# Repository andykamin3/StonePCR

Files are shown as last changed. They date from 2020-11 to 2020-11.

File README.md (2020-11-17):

# StonePCR
*Por Joaquín Alonso, Manuel Agustín Gonzalez y Andrés Kaminker*

## Introducción

### ¿Qué es una máquina de PCR?
También conocido como termociclador es un elemento esencial en laboratorios de biología molecular dado que permite realizar, los ciclos térmicos esenciales en la reacción en cadena de la polimerasa. Es por esto que son utilizados en múltiples procesos, uno de ellos es el test de COVID-19. 
Estos equipos pueden llegar a costar entre 2 y 50 mil dólares en nuestro [país](https://www.onelab.com.ar/pcr). Pese a eso existen alternativas libres como [OpenPCR](https://openpcr.org/) que resultan mucho más baratas. Este es un trabajo que busca ofrecer una alternativa similar a OpenPCR pero con mejores prestaciones a nivel técnico. 

## Selección de Componentes

### ARM Cortex M3

Este microcontrolador fue elegido dado que representaba un improvement por sobre el Atmega328 del OpenPCR. A su vez contaba con pines que soportaban los protocolos necesarios tal como I2C y SPI. Por último contaba con pines que soportaban la interfaz casi directa con un puerto USB, elemento altamente deseable para evitar complicaciones en el desarrollo de la interfaz. Por último, el ADC integrado era suficiente para la lectura de los sensores, proporcionando la precisión suficiente. 
- [Datasheet](https://www.st.com/resource/en/datasheet/stm32f102c8.pdf)
- [Guía de Comienzo Rápido](https://www.st.com/resource/en/application_note/cd00164185-getting-started-with-stm32f10xxx-hardware-development-stmicroelectronics.pdf)

### Comunicación con dispositivos externos

#### USB

En primer lugar dispusimos ofrecer comunicación con una computadora mediante USB-B Micro. De esta manera permitíamos el uso del mismo con un conector fácilmente disponible pero que no agregaba las consideraciones de diseño necesarias del estándar USB-C dado que las prestaciones ofrecidas por este(mayor velocidad y _power delivery_ no fueron consideradas necesarias). Esta interfaz tiene como objetivo ofrecer una configuración rápida y fácil desde la aplicación complementaria en el ordenador. 

#### Bluetooth

Aunque la conexión USB era suficiente, decidimos agregar un módulo Bluetooth (HC-05) que permita la conexión inalámbrica a una app _companion_ en un teléfono celular que facilite el trabajo del usuario y le ofrezca recordatorios y alarmas sin tener que estar permanentemente alerta. 

### Sensado de Temperatura

Para el sensado de temperatura decidimos utilizar termistores NTC ofrecidos por Vishay(Modelo: (NTCLE317E4103SBA [https://www.vishay.com/docs/29216/ntcle317e4103sba.pdf]) que tenían las características técnicas necesarias, especialmente la precisión. A través de un divisor resistivo y el ADC del ARM Cortex M3 obtenemos el valor de temperatura, necesario para realizar correctamente los ciclos térmicos. 

### Placas de Peltier y Drivers

Las placas de Peltier seleccionadas, componente esencial del sistema, fueron un componente complejo de seleccionar pero finalmente nos decantamos por [VT-127-1.0-1.3-71](https://tetech.com/wp-content/uploads/2019/03/VT-127-1.0-1.3-71.pdf) de Tetech. La temperatura soportada y la alta potencia que manejan las convirtieron en una opción idónea para el proceso seleccionado. Los drivers fueron seleccionados en función a las placas de Peltier y sus altos requerimientos eléctricos. Es por eso que el driver [VNH5019A](https://www.pololu.com/product/1449) de Pololu fue seleccionadop porque podía entregar la potencia necesaria y era relativamente asequible. 

### Módulo de Pantalla

Para simplificar el desarrollo de la interfaz de usuario y prescindir de una miríada de botones y perillas decidimos usar una pantalla táctil. Para ello fue seleccionado el módulo de Adafruit [ILI9341](https://www.adafruit.com/product/2478). De esta manera disponemos de una pantalla sin incurrir en complejidades extras.

### Alimentación

Debido a la complejidad que presenta la placa y siguiendo los pasos de OpenPCR nos decantamos por el uso de un conector ATX-24 y una fuente externa lo que facilita el routeo y nos provee de líneas de alimentación con poco ruido en 3.3V y 12V.

## Tareas Pendientes 

- [x] Esquemático
- [x] Placement
- Routeo

## Imágenes

Render 3D del PCB
- Render del PCB en 3D

## Instrucciones de Uso del Proyecto
- Realizar una descarga o clonar el repositorio de forma local
- Abrir usando KiCad 5.1.6

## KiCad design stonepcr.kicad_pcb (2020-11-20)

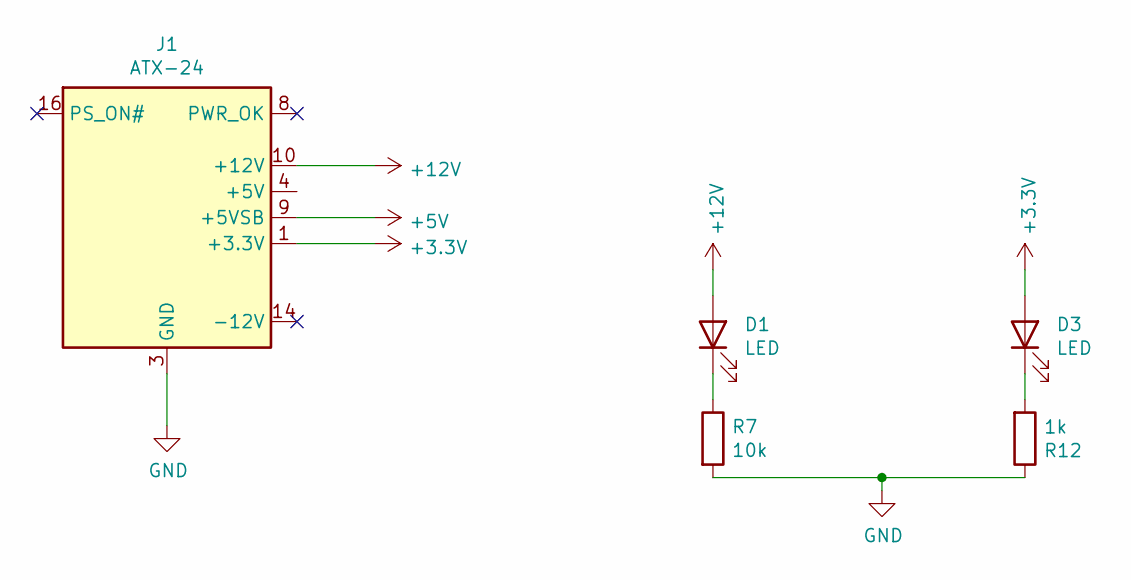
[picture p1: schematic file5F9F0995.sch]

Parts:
D1, D3: LED; LED_0805_2012Metric
J1: ATX-24; Molex_Mini-Fit_Jr_5566-24A_2x12_P4.20mm_Vertical
R7: 10k; R_0805_2012Metric
R12: 1k; R_0805_2012Metric

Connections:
+3V3: D3.2 (A), J1.1 (+3.3V), J1.2 (+3.3V), J1.12 (+3.3V), J1.13 (+3.3V); also elsewhere on the board
+5V: J1.9 (+5VSB)
+12V: D1.2 (A), J1.10 (+12V), J1.11 (+12V); also elsewhere on the board
GND: J1.3 (GND), J1.5 (GND), J1.7 (GND), J1.15 (GND), J1.17 (GND), J1.18 (GND), J1.19 (GND), J1.24 (GND), R7.2, R12.1; also elsewhere on the board
unnamed: D1.1 (K), R7.1
unnamed: D3.1 (K), R12.2
unnamed: J1.4 (+5V), J1.6 (+5V), J1.21 (+5V), J1.22 (+5V), J1.23 (+5V)

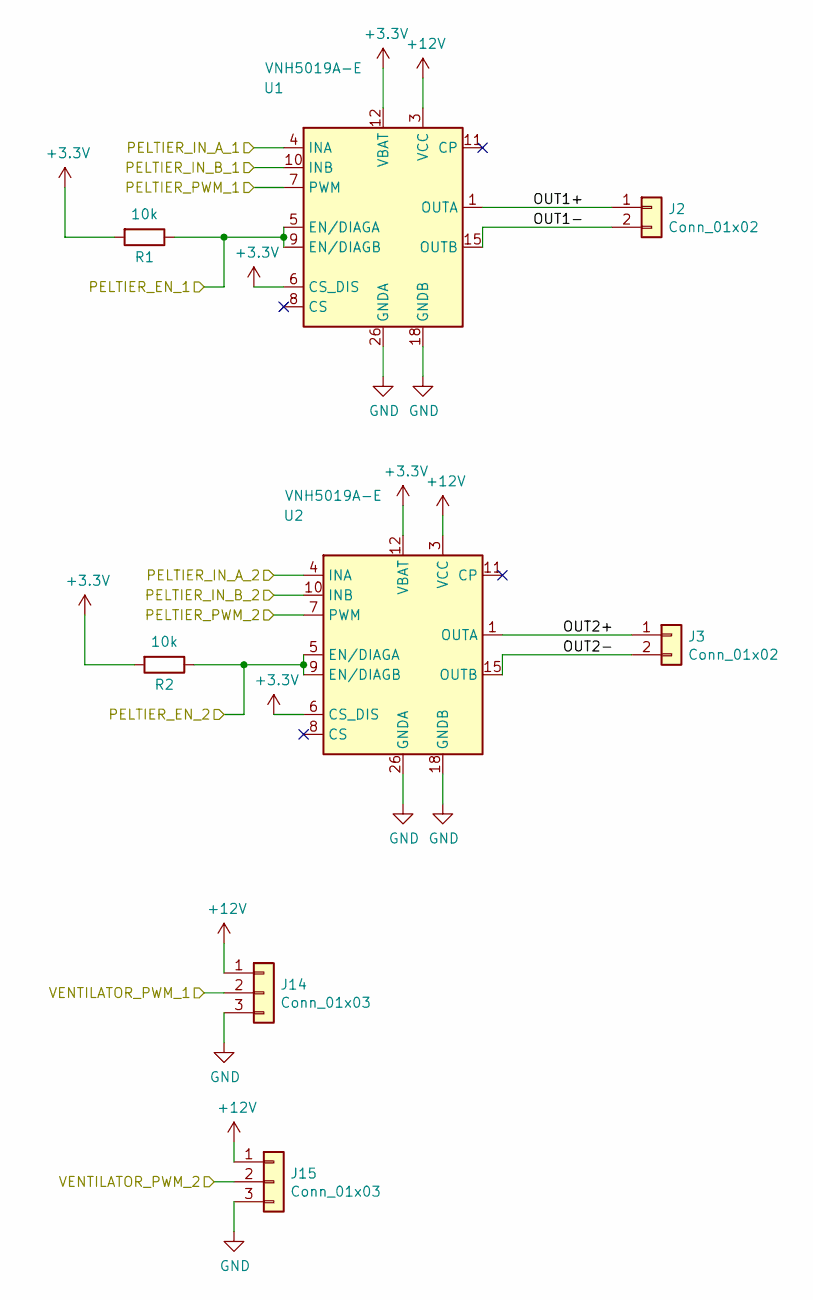
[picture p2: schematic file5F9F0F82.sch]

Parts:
J2, J3: Conn_01x02; Molex_Sabre_43160-0102_1x02_P7.49mm_Vertical_ThermalVias
J14, J15: Conn_01x03; PinSocket_1x03_P2.54mm_Vertical
R1, R2: 10k; R_0805_2012Metric
U1, U2: VNH5019A-E; ST_MultiPowerSO-30

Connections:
+3V3: R1.2, R2.2, U1.6 (CS_DIS), U1.12 (VBAT), U2.6 (CS_DIS), U2.12 (VBAT); also elsewhere on the board
+12V: J14.1, J15.1, U1.3 (VCC), U1.13 (VCC), U1.23 (VCC), U1.31 (VCC), U2.3 (VCC), U2.13 (VCC), U2.23 (VCC), U2.31 (VCC); also elsewhere on the board
/ControllerSchematic/PELTIER_EN_1: R1.1, U1.5 (EN/DIAGA), U1.9 (EN/DIAGB); also elsewhere on the board
/ControllerSchematic/PELTIER_EN_2: R2.1, U2.5 (EN/DIAGA), U2.9 (EN/DIAGB); also elsewhere on the board
/ControllerSchematic/PELTIER_IN_A_1: U1.4 (INA); also elsewhere on the board
/ControllerSchematic/PELTIER_IN_A_2: U2.4 (INA); also elsewhere on the board
/ControllerSchematic/PELTIER_IN_B_1: U1.10 (INB); also elsewhere on the board
/ControllerSchematic/PELTIER_IN_B_2: U2.10 (INB); also elsewhere on the board
/ControllerSchematic/PELTIER_PWM_1: U1.7 (PWM); also elsewhere on the board
/ControllerSchematic/PELTIER_PWM_2: U2.7 (PWM); also elsewhere on the board
/ControllerSchematic/VENTILADOR_PWM_1: J15.2; also elsewhere on the board
/ControllerSchematic/VENTILADOR_PWM_2: J14.2; also elsewhere on the board
/PeltierSchematic/OUT1+: J2.1, U1.1 (OUTA), U1.25 (OUTA), U1.30 (OUTA), U1.33 (OUTA)
/PeltierSchematic/OUT1-: J2.2, U1.15 (OUTB), U1.16 (OUTB), U1.21 (OUTB), U1.32 (OUTB)
/PeltierSchematic/OUT2+: J3.1, U2.1 (OUTA), U2.25 (OUTA), U2.30 (OUTA), U2.33 (OUTA)
/PeltierSchematic/OUT2-: J3.2, U2.15 (OUTB), U2.16 (OUTB), U2.21 (OUTB), U2.32 (OUTB)
GND: J14.3, J15.3, U1.18 (GNDB), U1.19 (GNDB), U1.20 (GNDB), U1.26 (GNDA), U1.27 (GNDA), U1.28 (GNDA), U2.18 (GNDB), U2.19 (GNDB), U2.20 (GNDB), U2.26 (GNDA), U2.27 (GNDA), U2.28 (GNDA); also elsewhere on the board

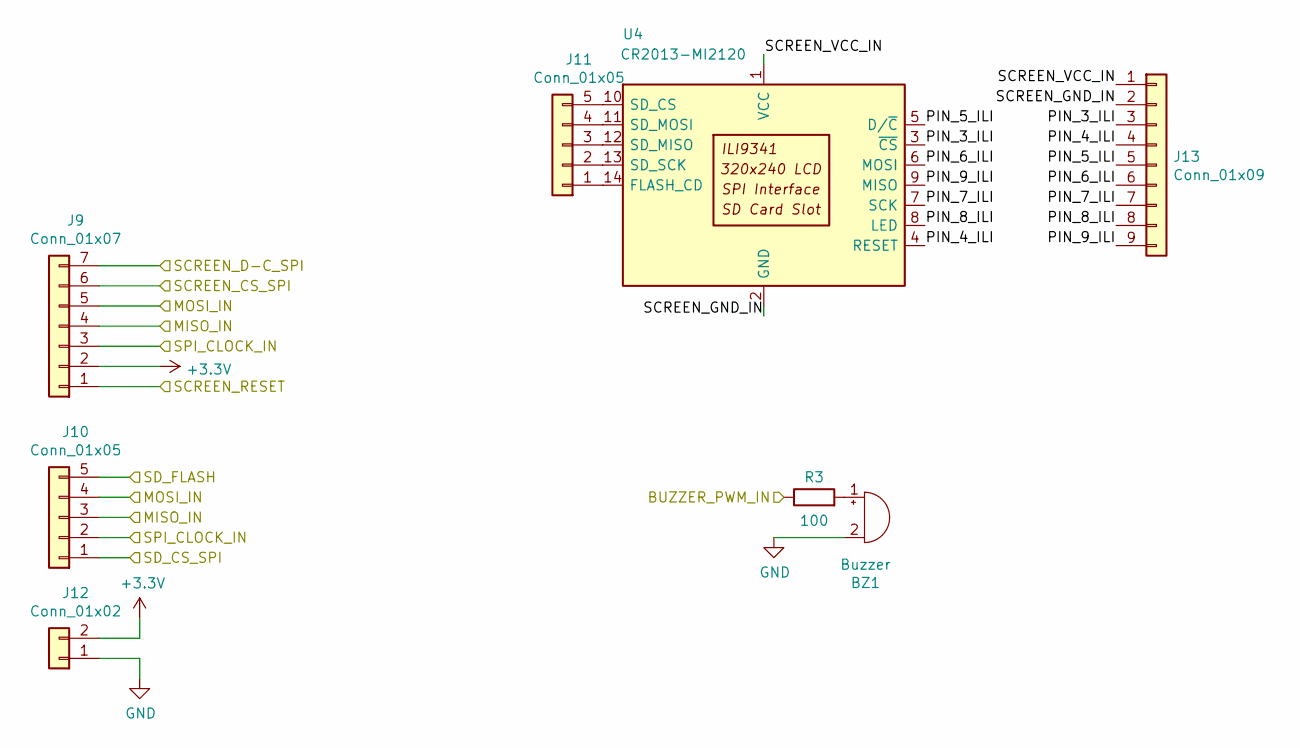
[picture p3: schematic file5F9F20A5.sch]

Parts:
BZ1: Buzzer; Buzzer_Mallory_AST1109MLTRQ
J9: Conn_01x07; PinSocket_1x07_P2.54mm_Vertical
J10, J11: Conn_01x05; PinSocket_1x05_P2.54mm_Vertical
J12: Conn_01x02; PinSocket_1x02_P2.54mm_Vertical
J13: Conn_01x09; PinSocket_1x09_P2.54mm_Vertical
R3: 100; R_0805_2012Metric
U4: CR2013-MI2120

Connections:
+3V3: J9.2, J12.2; also elsewhere on the board
/ControllerSchematic/BUZZER_PWM_IN: R3.1; also elsewhere on the board
/ControllerSchematic/SCREEN_CS_SPI: J9.6; also elsewhere on the board
/ControllerSchematic/SCREEN_D-C_SPI: J9.7; also elsewhere on the board
/ControllerSchematic/SCREEN_RESET: J9.1; also elsewhere on the board
/ControllerSchematic/SD_CS_SPI: J10.1; also elsewhere on the board
/ControllerSchematic/SD_FLASH: J10.5; also elsewhere on the board
/ControllerSchematic/SPI_CLOCK_IN: J9.3, J10.2; also elsewhere on the board
/DisplaySchematic/MISO_IN: J9.4, J10.3; also elsewhere on the board
/DisplaySchematic/MOSI_IN: J9.5, J10.4; also elsewhere on the board
/DisplaySchematic/PIN_3_ILI: J13.3, U4.3 (~CS)
/DisplaySchematic/PIN_4_ILI: J13.4, U4.4 (RESET)
/DisplaySchematic/PIN_5_ILI: J13.5, U4.5 (D/~C)
/DisplaySchematic/PIN_6_ILI: J13.6, U4.6 (MOSI)
/DisplaySchematic/PIN_7_ILI: J13.7, U4.7 (SCK)
/DisplaySchematic/PIN_8_ILI: J13.8, U4.8 (LED)
/DisplaySchematic/PIN_9_ILI: J13.9, U4.9 (MISO)
/DisplaySchematic/SCREEN_GND_IN: J13.2, U4.2 (GND)
/DisplaySchematic/SCREEN_VCC_IN: J13.1, U4.1 (VCC)
GND: BZ1.2 (+), J12.1; also elsewhere on the board
unnamed: BZ1.1 (-), R3.2
unnamed: J11.1, U4.14 (FLASH_CD)
unnamed: J11.2, U4.13 (SD_SCK)
unnamed: J11.3, U4.12 (SD_MISO)
unnamed: J11.4, U4.11 (SD_MOSI)
unnamed: J11.5, U4.10 (SD_CS)

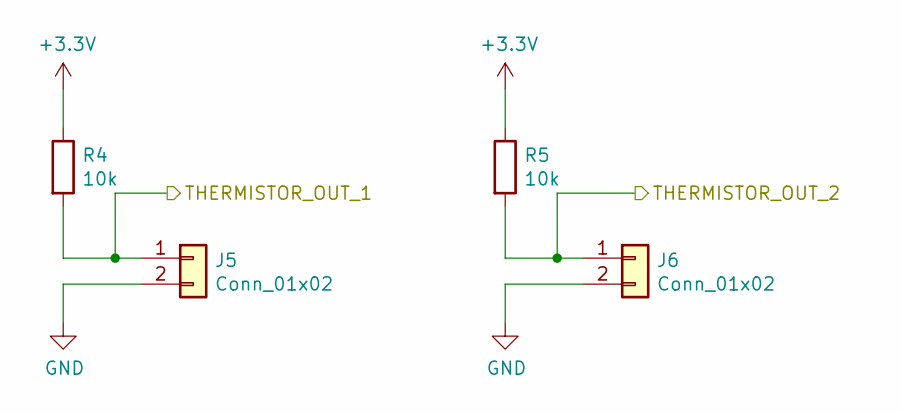
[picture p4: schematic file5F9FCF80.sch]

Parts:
J5, J6: Conn_01x02; PinHeader_1x02_P2.54mm_Vertical
R4, R5: 10k; R_0805_2012Metric

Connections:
+3V3: R4.1, R5.1; also elsewhere on the board
/ControllerSchematic/THERMISTOR_IN_1: J5.1, R4.2; also elsewhere on the board
/ControllerSchematic/THERMISTOR_IN_2: J6.1, R5.2; also elsewhere on the board
GND: J5.2, J6.2; also elsewhere on the board

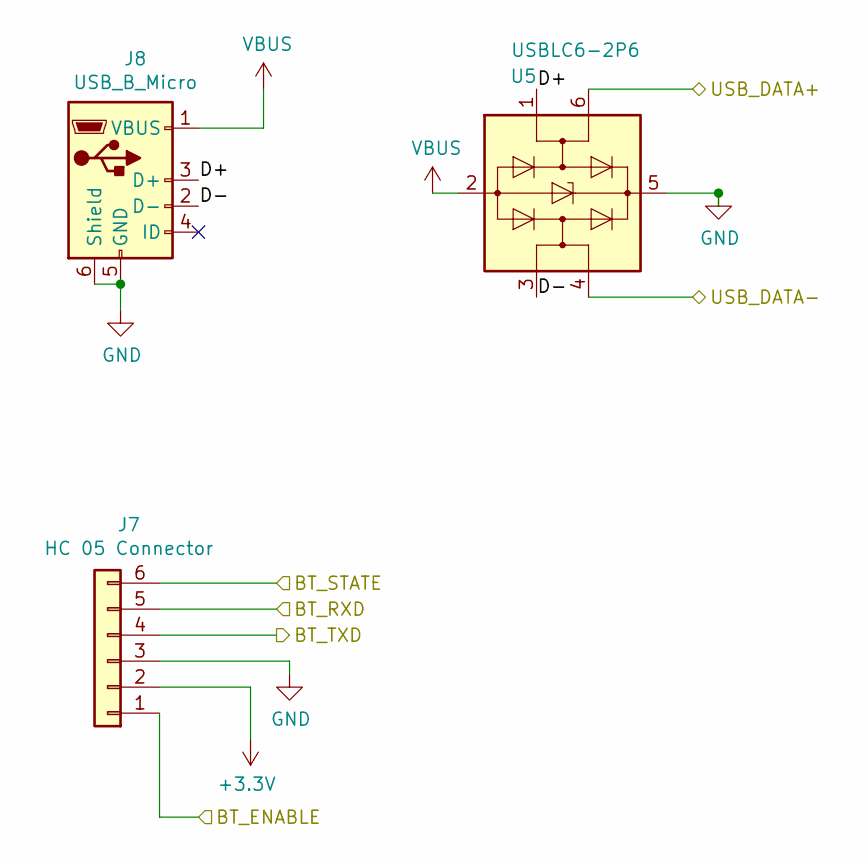
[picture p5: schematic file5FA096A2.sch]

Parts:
J7: HC 05 Connector; PinHeader_1x06_P2.54mm_Vertical
J8: USB_B_Micro; USB_Micro-B_Wuerth_629105150521
U5: USBLC6-2P6; SOT-666

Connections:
+3V3: J7.2; also elsewhere on the board
/ControllerSchematic/BT_ENABLE: J7.1; also elsewhere on the board
/ControllerSchematic/BT_RXD: J7.5; also elsewhere on the board
/ControllerSchematic/BT_STATE: J7.6; also elsewhere on the board
/ControllerSchematic/BT_TXD: J7.4; also elsewhere on the board
/ControllerSchematic/USB_DATA+: U5.6 (I/O1); also elsewhere on the board
/ControllerSchematic/USB_DATA-: U5.4 (I/O2); also elsewhere on the board
/InterfacesSchematic/D+: J8.3 (D+), U5.1 (I/O1)
/InterfacesSchematic/D-: J8.2 (D-), U5.3 (I/O2)
GND: J7.3, J8.5 (GND), J8.6 (Shield), U5.5 (VBUS); also elsewhere on the board
VBUS: J8.1 (VBUS), U5.2 (GND)

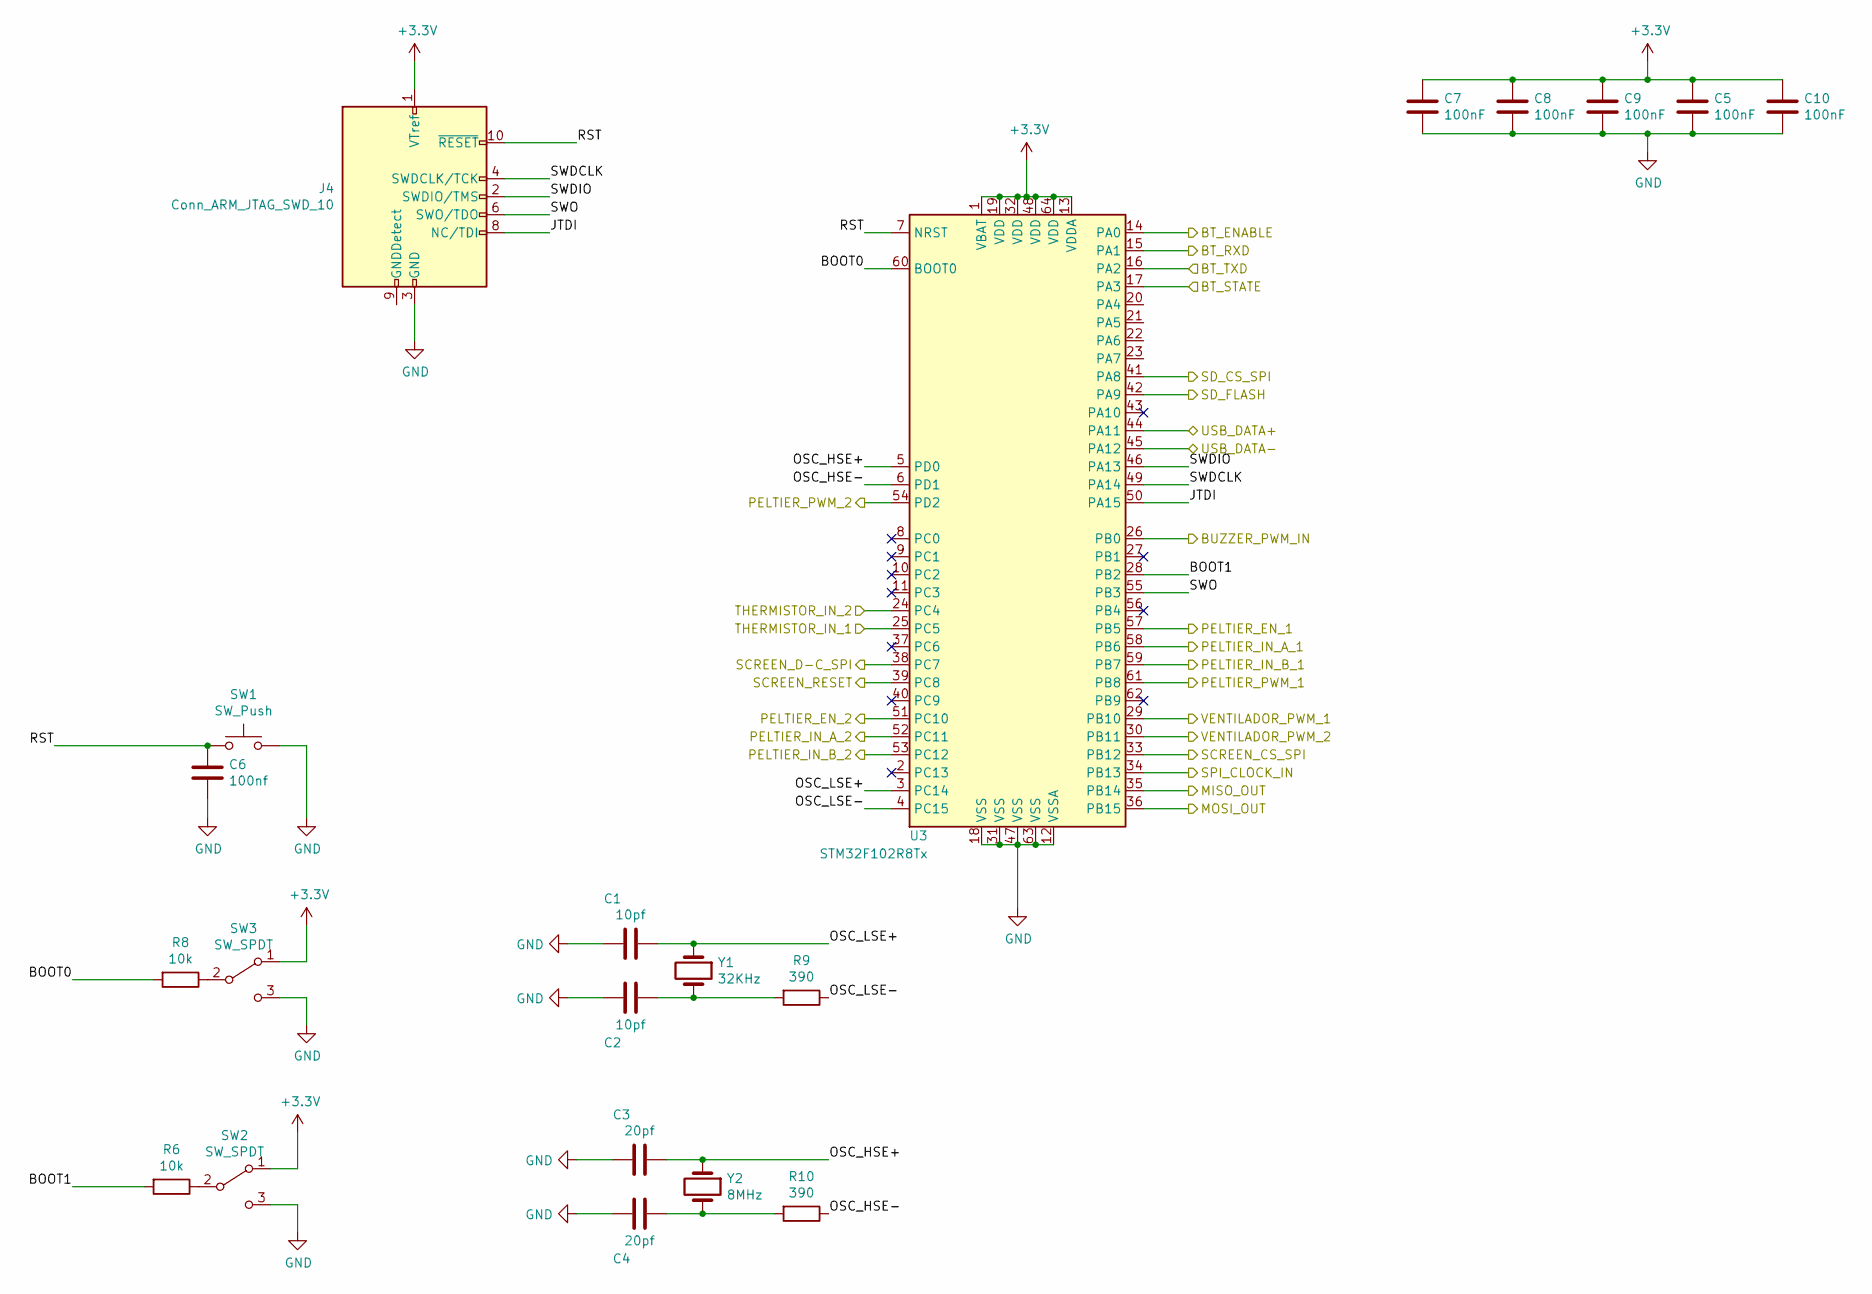
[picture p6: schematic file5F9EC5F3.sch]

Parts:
C1, C2: 10pf; C_0805_2012Metric
C3, C4: 20pf; C_0805_2012Metric
C5, C7, C8, C9, C10: 100nF; C_0805_2012Metric
C6: 100nf; C_0805_2012Metric
J4: Conn_ARM_JTAG_SWD_10; JST_EH_B10B-EH-A_1x10_P2.50mm_Vertical
R6, R8: 10k; R_0805_2012Metric
R9, R10: 390; R_0805_2012Metric
SW1: SW_Push; SW_SPST_CK_RS282G05A3
SW2, SW3: SW_SPDT; SW_SPDT_PCM12
U3: STM32F102R8Tx; LQFP-64_10x10mm_P0.5mm
Y1: 32KHz; Resonator-2Pin_W7.0mm_H2.5mm
Y2: 8MHz; Resonator-2Pin_W7.0mm_H2.5mm

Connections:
+3V3: C5.1, C7.1, C8.1, C9.1, C10.1, J4.1 (VTref), SW2.1 (A), SW3.1 (A), U3.1 (VBAT), U3.13 (VDDA), U3.19 (VDD), U3.32 (VDD), U3.48 (VDD), U3.64 (VDD); also elsewhere on the board
/ControllerSchematic/BOOT0: R8.2, U3.60 (BOOT0)
/ControllerSchematic/BOOT1: R6.2, U3.28 (PB2)
/ControllerSchematic/BT_ENABLE: U3.14 (PA0); also elsewhere on the board
/ControllerSchematic/BT_RXD: U3.15 (PA1); also elsewhere on the board
/ControllerSchematic/BT_STATE: U3.17 (PA3); also elsewhere on the board
/ControllerSchematic/BT_TXD: U3.16 (PA2); also elsewhere on the board
/ControllerSchematic/BUZZER_PWM_IN: U3.26 (PB0); also elsewhere on the board
/ControllerSchematic/JTDI: J4.8 (NC/TDI), U3.50 (PA15)
/ControllerSchematic/OSC_HSE+: C3.1, U3.5 (PD0), Y2.1
/ControllerSchematic/OSC_HSE-: R10.1, U3.6 (PD1)
/ControllerSchematic/OSC_LSE+: C1.1, U3.3 (PC14), Y1.1
/ControllerSchematic/OSC_LSE-: R9.1, U3.4 (PC15)
/ControllerSchematic/PELTIER_EN_1: U3.57 (PB5); also elsewhere on the board
/ControllerSchematic/PELTIER_EN_2: U3.51 (PC10); also elsewhere on the board
/ControllerSchematic/PELTIER_IN_A_1: U3.58 (PB6); also elsewhere on the board
/ControllerSchematic/PELTIER_IN_A_2: U3.52 (PC11); also elsewhere on the board
/ControllerSchematic/PELTIER_IN_B_1: U3.59 (PB7); also elsewhere on the board
/ControllerSchematic/PELTIER_IN_B_2: U3.53 (PC12); also elsewhere on the board
/ControllerSchematic/PELTIER_PWM_1: U3.61 (PB8); also elsewhere on the board
/ControllerSchematic/PELTIER_PWM_2: U3.54 (PD2); also elsewhere on the board
/ControllerSchematic/RST: C6.1, J4.10 (~RESET~), SW1.1, U3.7 (NRST)
/ControllerSchematic/SCREEN_CS_SPI: U3.33 (PB12); also elsewhere on the board
/ControllerSchematic/SCREEN_D-C_SPI: U3.38 (PC7); also elsewhere on the board
/ControllerSchematic/SCREEN_RESET: U3.39 (PC8); also elsewhere on the board
/ControllerSchematic/SD_CS_SPI: U3.41 (PA8); also elsewhere on the board
/ControllerSchematic/SD_FLASH: U3.42 (PA9); also elsewhere on the board
/ControllerSchematic/SPI_CLOCK_IN: U3.34 (PB13); also elsewhere on the board
/ControllerSchematic/SWDCLK: J4.4 (SWDCLK/TCK), U3.49 (PA14)
/ControllerSchematic/SWDIO: J4.2 (SWDIO/TMS), U3.46 (PA13)
/ControllerSchematic/SWO: J4.6 (SWO/TDO), U3.55 (PB3)
/ControllerSchematic/THERMISTOR_IN_1: U3.25 (PC5); also elsewhere on the board
/ControllerSchematic/THERMISTOR_IN_2: U3.24 (PC4); also elsewhere on the board
/ControllerSchematic/USB_DATA+: U3.44 (PA11); also elsewhere on the board
/ControllerSchematic/USB_DATA-: U3.45 (PA12); also elsewhere on the board
/ControllerSchematic/VENTILADOR_PWM_1: U3.29 (PB10); also elsewhere on the board
/ControllerSchematic/VENTILADOR_PWM_2: U3.30 (PB11); also elsewhere on the board
/DisplaySchematic/MISO_IN: U3.35 (PB14); also elsewhere on the board
/DisplaySchematic/MOSI_IN: U3.36 (PB15); also elsewhere on the board
GND: C1.2, C2.2, C3.2, C4.2, C5.2, C6.2, C7.2, C8.2, C9.2, C10.2, J4.3 (GND), J4.5 (GND), SW1.2, SW2.3 (C), SW3.3 (C), U3.12 (VSSA), U3.18 (VSS), U3.31 (VSS), U3.47 (VSS), U3.63 (VSS); also elsewhere on the board
unnamed: C2.1, R9.2, Y1.2
unnamed: C4.1, R10.2, Y2.2
unnamed: R6.1, SW2.2 (B)
unnamed: R8.1, SW3.2 (B)

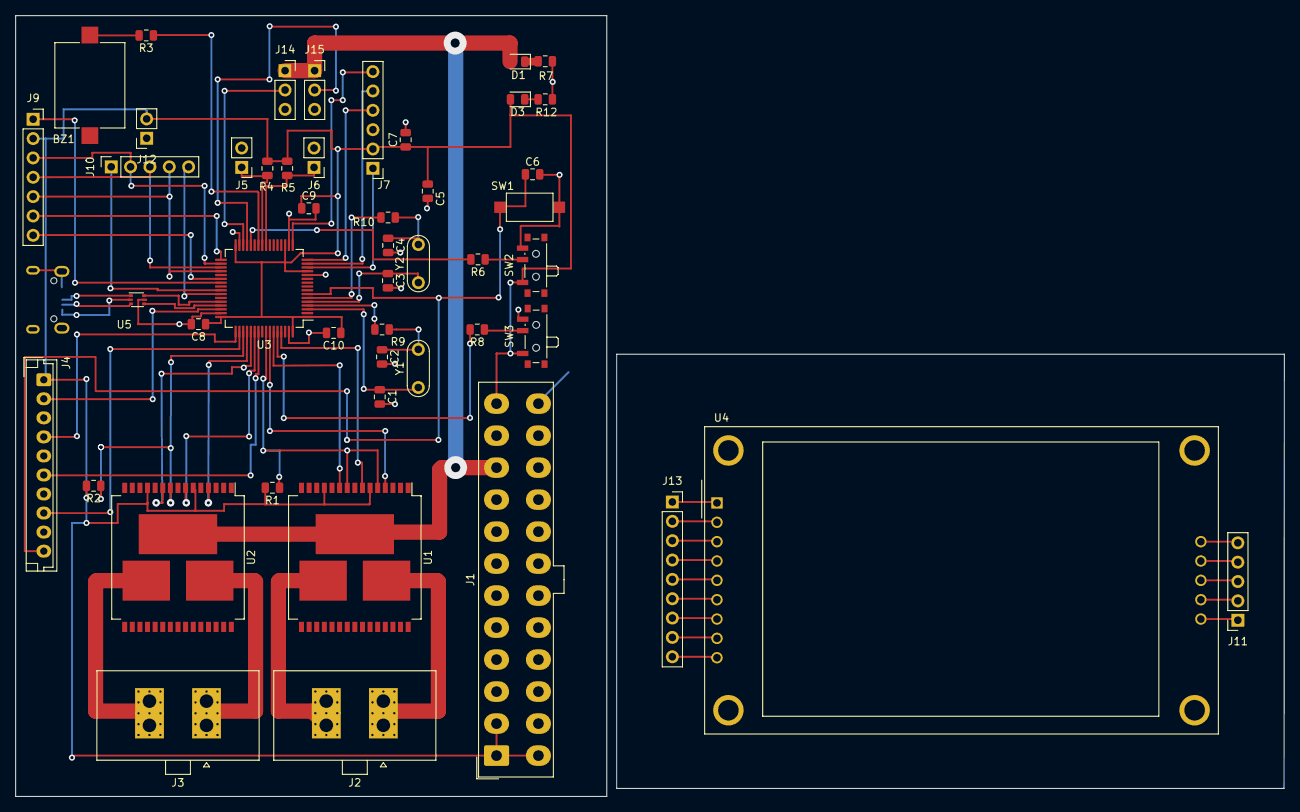
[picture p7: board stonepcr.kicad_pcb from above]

Board: 2 copper layers, 166.6 x 102.5 mm, 49 parts (1 on the bottom side), 70 nets.

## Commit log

2020-11-01 Initial commit
    :)
    [file5F9EC5F3.sch, file5F9F0995.sch, file5F9F0F82.sch, stonepcr.kicad_pcb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]
2020-11-01 Cosas
    - Power
    - I/O
    - Screen
    - Sensing
    [file5F9EC5F3.sch, file5F9F0995.sch, file5F9F0F82.sch, file5F9F20A5.sch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]
2020-11-04 Finished schematic
    [file5F9EC5F3.sch, file5F9F0F82.sch, file5F9F20A5.sch, file5F9FCF80.sch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]
2020-11-04 Added footprints
    [file5F9EC5F3.sch, file5F9F0995.sch, file5F9F0F82.sch, file5F9F20A5.sch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]
2020-11-16 Preparation for differential routing and small placement corrections.
    [file5F9EC5F3.sch, file5FA096A2.sch, stonepcr.kicad_pcb, stonepcr.sch]
2020-11-17 Trackeo
    Pobre trackeo parcial. Backup
    [file5F9EC5F3.sch, file5F9F0995.sch, file5F9F0F82.sch, stonepcr.kicad_pcb]
2020-11-17 Replacement and adjustments
    [stonepcr.kicad_pcb]
2020-11-17 Rotación Swithc
    [stonepcr.kicad_pcb]
2020-11-19 Initial Routing
    [stonepcr.kicad_pcb]
2020-11-19 Removal of LED 5V and further routing
    [file5F9EC5F3.sch, file5F9F0995.sch, stonepcr.kicad_pcb]
2020-11-20 Copper layer for logic
    [stonepcr.kicad_pcb]
